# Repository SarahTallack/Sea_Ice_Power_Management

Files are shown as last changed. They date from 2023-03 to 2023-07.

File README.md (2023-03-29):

# Sea Ice Power Management

## Overview: 

The below extract is from the vacwork advertisement: 

“This work feeds into the physical characterisation of sea ice using LiDAR and cameras to improve parameterisation of Earth System Models. A preliminary prototype rig was constructed for the SCALE Winter 2022 cruise to collect data from a Livox AVIA LiDAR (https://www.livoxtech.com/avia) and an Intel Realsense D455 Depth camera (https://www.intelrealsense.com/depth-camera-d455). During the SCALE cruise we were able to collect a comprehensive LiDAR/Realsense scan dataset of individual pancake ice floes which were collected and placed on deck. The goal of these vacation work positions is to improve the reliability and usability of the imaging rig to make it more robust for future experiments and cruises.” 

This project focuses on the design and improvement of the power management for the rig mentioned in the above. This report aims to outline the process taken to understand the power requirements of the system, as well as to research possible methods for supplying power in cold weather (-20°C). 

## Design Process and Decisions 

Before exploring methods for supplying power, it is important to understand the power requirements of the system. Thus, the first step is to research individual components and determine what voltages they are able to operate at and draw up a power budget for the system. The power budget for the system is shown in the following section. 

Once a power budget had been compiled, a meeting was had to discuss the best methods for supplying power to the system. It was decided that a battery supply such a EcoFlow or Jackery would be the most robust and allow other groups to use the supply if needed. Since these batteries are Lithium-Ion, which operate best at room-temperature, a temperature controller enclosure needs to be designed for the battery. Additionally, the team wanted the system to be able to be powered from mains or from the battery, and to be able to easily switch between these two options. 

Thus, two separate circuits need to be designed. The first should be able to distribute a single supply to at least two devices, as well as to switch between either mains or a battery as the power supply. The second design needed to control the temperature of the box, using a microcontroller, sensors and heating pads. 

## Power Budget

The power budget can be found in an excel spreadsheet called PowerBudget.

## Power Distribution

### Basic Operation

Two devices needed to be power by a single source, namely an Intel NUC (mini-PC) and a Livox AVIA. These devices needed to either be powered by a main supply, via an AC/DC supply, or by a DC output from a battery supply. 

The user should be able to switch between the two supplies and turn everything off. A panel mounted switch is to be connected via the switch header pins (J6). An external LED indicator is connected in a similar fashion, using the J7 pins.  

A MOSFET configuration is used for switching when power is supplied, and the switch is ON. When Q1 is turned on, it allows Q2 to be turned on, which then provides power to the external jacks. Fuses are added to the output of each supply. 

Component Selection 

The input jacks had to be selected to ensure they could withstand up to 8A. 8A fuses are placed to ensure the circuit is not overloaded. Schottky diodes are chosen that can withstand the current to be supplied. 

N-channel MOSFETs are chosen for low current switching, and the P-channel MOSFET is selected as it can withstand high currents. The DC jacks at the output are selected to withstand up to 5A of current, which is the maximum current draw of the devices to be powered. 

### KiCAD project files

The project files for this board can be found in "\PCB Design\Power Distribution".

## Temperature Controller

### Basic Operation

The PCB is designed to fit onto an STM32 Nucleo-64 microcontroller. It is designed to read a temperature controller and implement a bang-bang controller to maintain the ambient temperature in an enclosure between a lower and upper temperature value, by switching external heating pads on or off.  

An RTD sensor is used in a Wheatstone bridge configuration, and the two outputs of the bridge are sent into an instrumentation amplifier (U1). The output of the instrumentation amplifier is sent to an ADC pin on the Nucleo. The Nucleo then converts this ADC value into a temperature. Depending on this temperature value, the heaters are either turned on or off.  

A GPIO output pin is used in conjunction with a MOSFET switching circuit, to supply an external power source to the heating pads, as the pads could not be powered by the microcontroller. 

A pushbutton is used to turn on and off the control, and an indicator is used to show if the system is operational or not.  

### KiCAD project files

The project files for this board can be found in "\PCB Design\Temperature Controller".

### STM Nucleo-64 Code

The code used for the temperature controller can be found in "\Temperature Control Code\TemperatureController".

## Component Selection and Calculations
Most calculations were done using the TemperatureSensorValues.mlx file. 

## Assembly and Testing of boards

## Other components needed

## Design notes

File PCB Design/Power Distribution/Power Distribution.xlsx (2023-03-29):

Source:,"C:\Users\sarah\Documents\sea-ice-power-management\PCB Design\Power Distribution\Power Distribution.kicad_sch"
Date:,"2022/12/08 15:22:51"
Tool:,"Eeschema (6.0.8)"
Generator:,"C:\Program Files\KiCad\6.0\bin\scripting\plugins/bom_csv_grouped_by_value.py"
Component Count:,"27"
Individual Components:
Item,"Qty","Reference(s)","Value","LibPart","Footprint","Datasheet","LCSC No.","Price"
,"","C1","10n","Device:C_Small","Capacitor_SMD:C_0805_2012Metric","https://datasheet.lcsc.com/lcsc/1811151136_Samsung-Electro-Mechanics-CL21B103KBANNNC_C1710.pdf","C1710","0.0062"
,"","C2","10n","Device:C_Small","Capacitor_SMD:C_0805_2012Metric","https://datasheet.lcsc.com/lcsc/1811151136_Samsung-Electro-Mechanics-CL21B103KBANNNC_C1710.pdf","C1710","0.0062"
,"","C3","100n","Device:C_Small","Capacitor_SMD:C_0805_2012Metric","https://datasheet.lcsc.com/lcsc/1810101813_YAGEO-CC0805KRX7R9BB104_C49678.pdf","C49678","0.0036"
,"","C4","4.7u","Device:C_Small","Capacitor_SMD:C_1206_3216Metric","https://datasheet.lcsc.com/lcsc/1811091112_FH--Guangdong-Fenghua-Advanced-Tech-1206B475K500NT_C29823.pdf","C29823","0.0091"
,"","D1","D_Schottky","Device:D_Schottky","Footprints:Schottky Diode SK1010C","https://datasheet.lcsc.com/lcsc/2012211036_MDD-Microdiode-Electronics--SK1010C_C65020.pdf","C65020","0.1616"
,"","D2","D_Schottky","Device:D_Schottky","Footprints:Schottky Diode SK1010C","https://datasheet.lcsc.com/lcsc/2012211036_MDD-Microdiode-Electronics--SK1010C_C65020.pdf","C65020","0.1616"
,"","F1","Fuse","Device:Fuse","Footprints:FUSE Holder ROHS","https://datasheet.lcsc.com/lcsc/1811061209_Xucheng-Elec-C3131_C3131.pdf","C3131","0.0590"
,"","F2","Fuse","Device:Fuse","Footprints:FUSE Holder ROHS","https://datasheet.lcsc.com/lcsc/1811061209_Xucheng-Elec-C3131_C3131.pdf","C3131","0.0590"
,"","J1","Barrel_Jack",":Barrel_Jack_1","Footprints:CONN-TH_XT60PW-M","https://datasheet.lcsc.com/lcsc/1810251313_Changzhou-Amass-Elec-XT60PW-M_C98732.pdf","C98732","0.3915"
,"","J2","Barrel_Jack",":Barrel_Jack_1","Footprints:CONN-TH_XT60PW-M","https://datasheet.lcsc.com/lcsc/1810251313_Changzhou-Amass-Elec-XT60PW-M_C98732.pdf","C98732","0.3915"
,"","J3","Barrel_Jack","SarahLibrary:Barrel_Jack","Footprints:DC Jack 5A","https://datasheet.lcsc.com/lcsc/2110151730_XKB-Connectivity-DC-005-5A-3-0_C388625.pdf","C388625","0.2379"
,"","J4","Barrel_Jack","SarahLibrary:Barrel_Jack","Footprints:DC Jack 5A","https://datasheet.lcsc.com/lcsc/2110151730_XKB-Connectivity-DC-005-5A-3-0_C388625.pdf","C388625","0.2379"
,"","J5","Barrel_Jack","SarahLibrary:Barrel_Jack","Footprints:DC Jack 5A","https://datasheet.lcsc.com/lcsc/2110151730_XKB-Connectivity-DC-005-5A-3-0_C388625.pdf","C388625","0.2379"
,"","J6","Switch Header Pin","Connector:Conn_01x03_Male","Footprints:3 Pin Male Header","https://datasheet.lcsc.com/lcsc/1811021622_BOOMELE-Boom-Precision-Elec-VH-3A_C20547.pdf","C20547","0.0303"
,"","J7","Conn_01x02_Male","Connector:Conn_01x02_Male","Footprints:2 Pin Male Header","https://datasheet.lcsc.com/lcsc/1811132110_BOOMELE-Boom-Precision-Elec-XH-2A_C20079.pdf","C20079","0.0058"
,"","Q1","2N7002","Transistor_FET:2N7002","Package_TO_SOT_SMD:SOT-23","https://datasheet.lcsc.com/lcsc/1810151612_Jiangsu-Changjing-Electronics-Technology-Co---Ltd--2N7002_C8545.pdf","C8545","0.0149"
,"","Q2","NCE30P30K","SarahLibrary:NCE30P30K","Footprints:NCE30P30K P channel MOSFET","https://datasheet.lcsc.com/lcsc/1811041601_Wuxi-NCE-Power-Semiconductor-NCE30P30K_C130106.pdf","C130106","0.1349"
,"","Q3","2N7002","Transistor_FET:2N7002","Package_TO_SOT_SMD:SOT-23","https://datasheet.lcsc.com/lcsc/1810151612_Jiangsu-Changjing-Electronics-Technology-Co---Ltd--2N7002_C8545.pdf","C8545","0.0149"
,"","R1","330k","Device:R","Resistor_SMD:R_0805_2012Metric","https://datasheet.lcsc.com/lcsc/2205311830_UNI-ROYAL-Uniroyal-Elec-0805W8F3303T5E_C17629.pdf","C17629","0.0015"
,"","R2","10k","Device:R","Resistor_SMD:R_0805_2012Metric","https://datasheet.lcsc.com/lcsc/2206010216_UNI-ROYAL-Uniroyal-Elec-0805W8F1002T5E_C17414.pdf","C17414","0.0008"
,"","R3","100k","Device:R","Resistor_SMD:R_0805_2012Metric","https://datasheet.lcsc.com/lcsc/2205312316_UNI-ROYAL-Uniroyal-Elec-0805W8F1003T5E_C149504.pdf","C149504","0.0016"
,"","R4","82k","Device:R","Resistor_SMD:R_0805_2012Metric","https://datasheet.lcsc.com/lcsc/2205311830_UNI-ROYAL-Uniroyal-Elec-0805W8F8202T5E_C17840.pdf","C17840","0.0016"
,"","R5","100k","Device:R","Resistor_SMD:R_0805_2012Metric","https://datasheet.lcsc.com/lcsc/2205312316_UNI-ROYAL-Uniroyal-Elec-0805W8F1003T5E_C149504.pdf","C149504","0.0016"
,"","R6","1.8k","Device:R","Resistor_SMD:R_0805_2012Metric","https://datasheet.lcsc.com/lcsc/2206010216_UNI-ROYAL-Uniroyal-Elec-0805W8F1801T5E_C17398.pdf","C17398","0.0016"
,"","TP1","TestPoint","Connector:TestPoint","TestPoint:TestPoint_Plated_Hole_D2.0mm","~","",""
,"","TP2","TestPoint","Connector:TestPoint","TestPoint:TestPoint_Plated_Hole_D2.0mm","~","",""
,"","TP3","TestPoint","Connector:TestPoint","TestPoint:TestPoint_Plated_Hole_D2.0mm","~","",""
Collated Components:
Item,"Qty","Reference(s)","Value","LibPart","Footprint","Datasheet","LCSC No.","Price"
1,"2","C1, C2","10n","Device:C_Small","Capacitor_SMD:C_0805_2012Metric","https://datasheet.lcsc.com/lcsc/1811151136_Samsung-Electro-Mechanics-CL21B103KBANNNC_C1710.pdf","C1710","0.0062"
2,"1","C3","100n","Device:C_Small","Capacitor_SMD:C_0805_2012Metric","https://datasheet.lcsc.com/lcsc/1810101813_YAGEO-CC0805KRX7R9BB104_C49678.pdf","C49678","0.0036"
3,"1","C4","4.7u","Device:C_Small","Capacitor_SMD:C_1206_3216Metric","https://datasheet.lcsc.com/lcsc/1811091112_FH--Guangdong-Fenghua-Advanced-Tech-1206B475K500NT_C29823.pdf","C29823","0.0091"
4,"2","D1, D2","D_Schottky","Device:D_Schottky","Footprints:Schottky Diode SK1010C","https://datasheet.lcsc.com/lcsc/2012211036_MDD-Microdiode-Electronics--SK1010C_C65020.pdf","C65020","0.1616"
5,"2","F1, F2","Fuse","Device:Fuse","Footprints:FUSE Holder ROHS","https://datasheet.lcsc.com/lcsc/1811061209_Xucheng-Elec-C3131_C3131.pdf","C3131","0.0590"
6,"2","J1, J2","Barrel_Jack",":Barrel_Jack_1","Footprints:CONN-TH_XT60PW-M","https://datasheet.lcsc.com/lcsc/1810251313_Changzhou-Amass-Elec-XT60PW-M_C98732.pdf","C98732","0.3915"
7,"3","J3, J4, J5","Barrel_Jack","SarahLibrary:Barrel_Jack","Footprints:DC Jack 5A","https://datasheet.lcsc.com/lcsc/2110151730_XKB-Connectivity-DC-005-5A-3-0_C388625.pdf","C388625","0.2379"
8,"1","J6","Switch Header Pin","Connector:Conn_01x03_Male","Footprints:3 Pin Male Header","https://datasheet.lcsc.com/lcsc/1811021622_BOOMELE-Boom-Precision-Elec-VH-3A_C20547.pdf","C20547","0.0303"
9,"1","J7","Conn_01x02_Male","Connector:Conn_01x02_Male","Footprints:2 Pin Male Header","https://datasheet.lcsc.com/lcsc/1811132110_BOOMELE-Boom-Precision-Elec-XH-2A_C20079.pdf","C20079","0.0058"
10,"2","Q1, Q3","2N7002","Transistor_FET:2N7002","Package_TO_SOT_SMD:SOT-23","https://datasheet.lcsc.com/lcsc/1810151612_Jiangsu-Changjing-Electronics-Technology-Co---Ltd--2N7002_C8545.pdf","C8545","0.0149"
11,"1","Q2","NCE30P30K","SarahLibrary:NCE30P30K","Footprints:NCE30P30K P channel MOSFET","https://datasheet.lcsc.com/lcsc/1811041601_Wuxi-NCE-Power-Semiconductor-NCE30P30K_C130106.pdf","C130106","0.1349"
12,"1","R1","330k","Device:R","Resistor_SMD:R_0805_2012Metric","https://datasheet.lcsc.com/lcsc/2205311830_UNI-ROYAL-Uniroyal-Elec-0805W8F3303T5E_C17629.pdf","C17629","0.0015"
13,"1","R2","10k","Device:R","Resistor_SMD:R_0805_2012Metric","https://datasheet.lcsc.com/lcsc/2206010216_UNI-ROYAL-Uniroyal-Elec-0805W8F1002T5E_C17414.pdf","C17414","0.0008"
14,"2","R3, R5","100k","Device:R","Resistor_SMD:R_0805_2012Metric","https://datasheet.lcsc.com/lcsc/2205312316_UNI-ROYAL-Uniroyal-Elec-0805W8F1003T5E_C149504.pdf","C149504","0.0016"
15,"1","R4","82k","Device:R","Resistor_SMD:R_0805_2012Metric","https://datasheet.lcsc.com/lcsc/2205311830_UNI-ROYAL-Uniroyal-Elec-0805W8F8202T5E_C17840.pdf","C17840","0.0016"
16,"1","R6","1.8k","Device:R","Resistor_SMD:R_0805_2012Metric","https://datasheet.lcsc.com/lcsc/2206010216_UNI-ROYAL-Uniroyal-Elec-0805W8F1801T5E_C17398.pdf","C17398","0.0016"
17,"3","TP1, TP2, TP3","TestPoint","Connector:TestPoint","TestPoint:TestPoint_Plated_Hole_D2.0mm","~","",""

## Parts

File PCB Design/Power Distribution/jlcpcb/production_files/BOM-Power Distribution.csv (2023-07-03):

Comment | Designator | Footprint | LCSC
NCE30P30K | Q2 | TO-252-2 | C130106
10n | C1,C2 | C_0402_1005Metric | C15195
1.8k | R6 | R_0805_2012Metric | C17398
82k | R4 | R_0805_2012Metric | C17840
LED | J7 | 2 Pin Male Header | C20079
Switch Header Pin | J6 | PinHeader_1x03_P2.54mm_Vertical | C20547
100k | R3,R5 | R_0402_1005Metric | C25741
10k | R2 | R_0402_1005Metric | C25744
330k | R1 | R_0402_1005Metric | C25778
4.7u | C4 | C_1206_3216Metric | C29823
100n | C3 | C_0402_1005Metric | C307331
Fuse | F1,F2 | FUSE Holder ROHS | C3131
Barrel_Jack | J3,J4,J5 | DC Jack 5A | C388625
D_Schottky | D1,D2 | Schottky Diode SK1010C | C65020
2N7002 | Q1,Q3 | SOT-23 | C8545
Barrel_Jack | J1,J2 | CONN-TH_XT60PW-M | C98732
TestPoint | TP1 | TestPoint_THTPad_D1.0mm_Drill0.5mm
TestPoint | TP2 | TestPoint_THTPad_D1.0mm_Drill0.5mm
TestPoint | TP3 | TestPoint_THTPad_D1.0mm_Drill0.5mm
Conn_01x02_Pin | J8 | PinHeader_1x02_P2.54mm_Vertical
Conn_01x02_Pin | J9 | PinHeader_1x02_P2.54mm_Vertical

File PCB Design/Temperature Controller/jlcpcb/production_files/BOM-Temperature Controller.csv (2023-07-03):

Comment | Designator | Footprint | LCSC
CJ431 | U2 | SOT-23 | C171428
INA332 | U1 | VSSOP-8_3.0x3.0mm_P0.65mm | C181461
PT100 Header Pins | J1,J2,J3 | 2 Pin Male Header | C20079
S8050_SMD | Q3 | SOT-23 | C2146
1.1k | R7 | R_0603_1608Metric | C22764
1.2k | R12,R6 | R_0603_1608Metric | C22765
Red | D2 | D_0603_1608Metric | C2286
27k | R5 | R_0603_1608Metric | C22967
3.3k | R1,R2 | R_0603_1608Metric | C22978
10k | R8 | R_0603_1608Metric | C25804
91 | R3 | R_0603_1608Metric | C2960792
SANYOU_SRD_Form_C | K1 | Relay_SPDT_SANYOU_SRD_Series_Form_C | C35449
Barrel_Jack | J5 | DC Jack 5A | C388625
Conn_01x03_Male | J8 | TerminalBlock_Altech_AK300-3_P5.00mm | C72334
1N5819 | D1 | D_SOD-123 | C8598
10u | C4 | C_0603_1608Metric | C96446
TestPoint | TP5 | TestPoint_THTPad_D1.0mm_Drill0.5mm
TestPoint | TP9 | TestPoint_Pad_D1.5mm
TestPoint | TP2 | TestPoint_THTPad_D1.0mm_Drill0.5mm
TestPoint | TP7 | TestPoint_THTPad_D1.0mm_Drill0.5mm
TestPoint | TP8 | TestPoint_Pad_D1.5mm
TestPoint | TP6 | TestPoint_THTPad_D1.0mm_Drill0.5mm
TestPoint | TP4 | TestPoint_THTPad_D1.0mm_Drill0.5mm
TestPoint | TP1 | TestPoint_THTPad_D1.0mm_Drill0.5mm
TestPoint | TP3 | TestPoint_THTPad_D1.0mm_Drill0.5mm
Conn_01x19_Female | J7 | PinSocket_1x19_P2.54mm_Vertical
Conn_01x19_Female | J6 | PinSocket_1x19_P2.54mm_Vertical

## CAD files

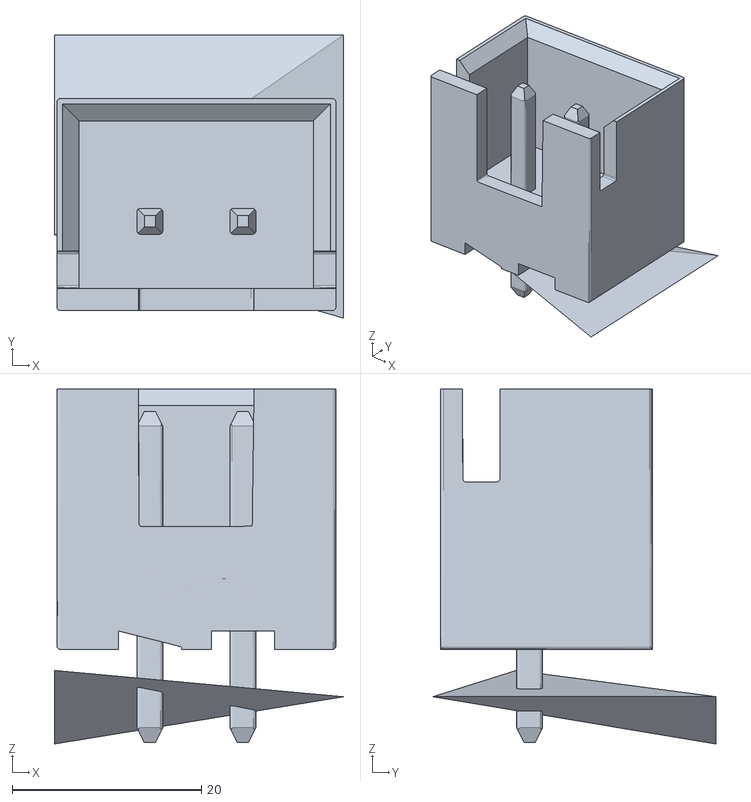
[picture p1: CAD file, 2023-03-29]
PCB Design/3D Model/2 Pin Header.obj
30.6 x 30.0 x 37.6

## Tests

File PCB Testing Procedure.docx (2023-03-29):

## Power Distribution

Circuits have been built/tested on a breadboard before ordering PCB. Theoretically should work.

### Steps for testing (before power)

1. Check that all components are populated that needed to be (also check orientation if applicable) - if there are any missing then these should be added before continuing.
2. Check most basic connections using test points and terminals.

The following tests should be done without inserting the fuses or connecting anything to the outputs.

### Test 1: check input (no fuse inserted)

1. Check that the input terminal works (was the actual circuit correct). If V+ and ground are connected is that what the board will get supplied with.

### Test 2: testing the switching circuit

1. Check resistor values.
2. Connect 12V to the Supply test point (probably should have had header pins here instead of a test point).
3. Check that the toggle switch works as expected with circuit.
4. Check that following is true:
5. Connect LED to J7 and check that it also only switches on when Vout is high.

### Test 3: check output

1. Supply voltage to Vout and check that barrel jacks at output have this voltage. Once again would have been useful to have header pins here instead of just a testpoint.
2. Barrel jacks should have V+ in centre rod and GND on the outer ring (bottom connector)

### Notes

- Should have included more header pins, especially for powering the circuits separately for testing and fault finding.

## Temperature Controller

### Steps for testing (before power)

1. Check that all components are populated that needed to be (also check orientation if applicable) - if there are any missing then these should be added before continuing.
2. Check most basic connections using test points and terminals.

Unit tests for temperature controller PCB

### Test 1: check wheatstone bridge

1. Check that resistor values.
2. Connect PT100 (need to get MOLEX connectors for this) or could use potentiometer to vary this value manually – just need to ensure that the resistor values from the pot are the same as range expected for PT100.

### Test 2: Instrumentation amplifier testing

1. If all connections are correct can power using +3V3 (this circuit is only connected to the wheatstone bridge)
2. Vary the voltage at Va (can either use jumpers and breadboard connected to J1 and manually swap out resistors or use a potentiometer).
3. Scope TempReading testpoint and compare value for various resistors to the expected/calculated values (should have a MATLAB script to do this).

### Test 3: inputs and outputs

1. Check connections and resistor values.
2. Connect the push button and LED and check that the circuit works.
3. Check barrel jack connections.

### Test 4: Relay circuit

1. Missing components are for the relay circuit – just need to talk to Justin about this.
2. Check that switching circuit works with a voltage of 3V3 at PD2 (this would be from the microcontroller).
3. Check that voltage across COM and NO only go high when PD2 goes high.

### Test 5: Temperature control code

1. Retest code developed previously.
2. Connect output from instrumentation amplifier only – use UART to print out the values being read for specific resistors values (check that ADC and code works properly). Should use same resistors/values as in test 2 step 3.
3. Disconnect instrumentation output. Connect the GPIO pins to the push button and LED and check that these work with code.
4. Check that the orientation of the board is correct so that it can fit onto the STM Nucleo.

### Notes

- Board was designed to use be power by the Nucleo via the micro-USB.
- Barrel jack power input is only for the relay circuit.
- Looking back – would have added a voltage regulator circuit to get a 5V output from the 12V which could be used to power the board and supply power to the relays.

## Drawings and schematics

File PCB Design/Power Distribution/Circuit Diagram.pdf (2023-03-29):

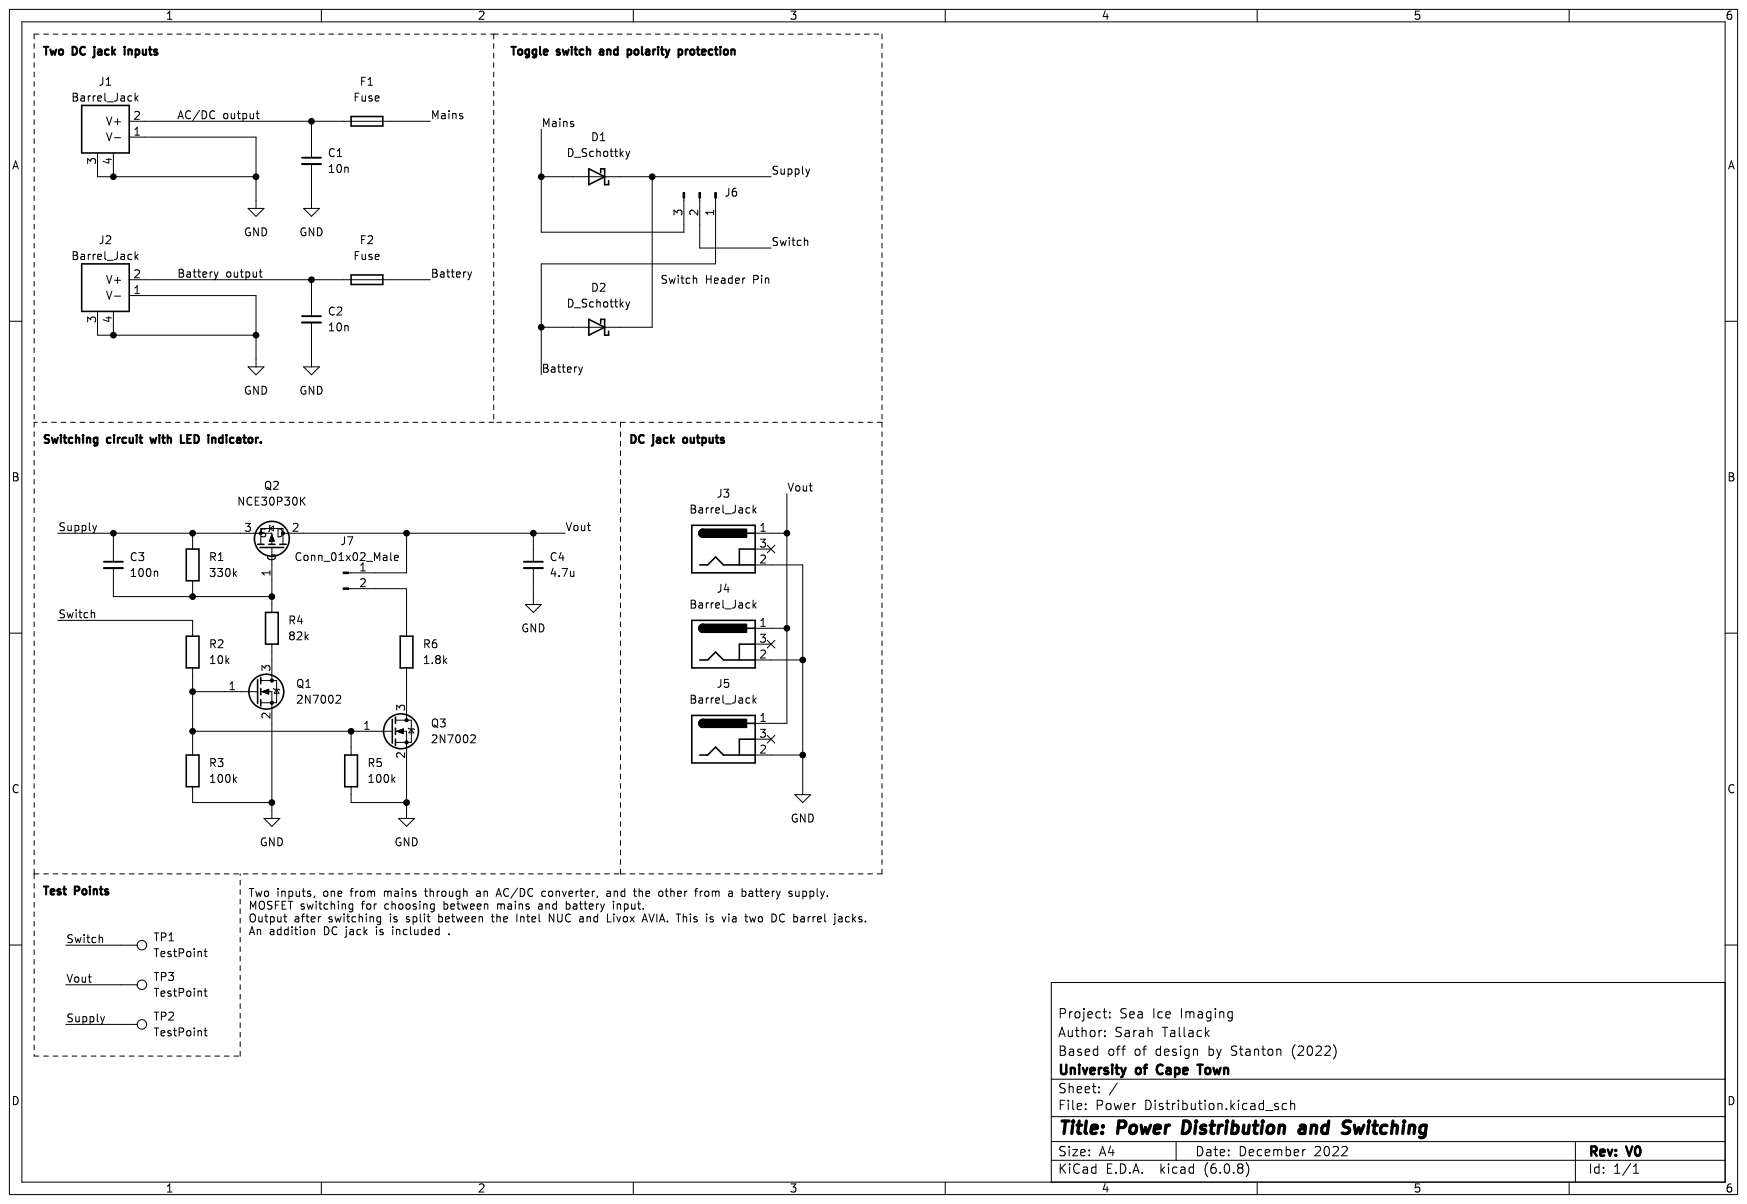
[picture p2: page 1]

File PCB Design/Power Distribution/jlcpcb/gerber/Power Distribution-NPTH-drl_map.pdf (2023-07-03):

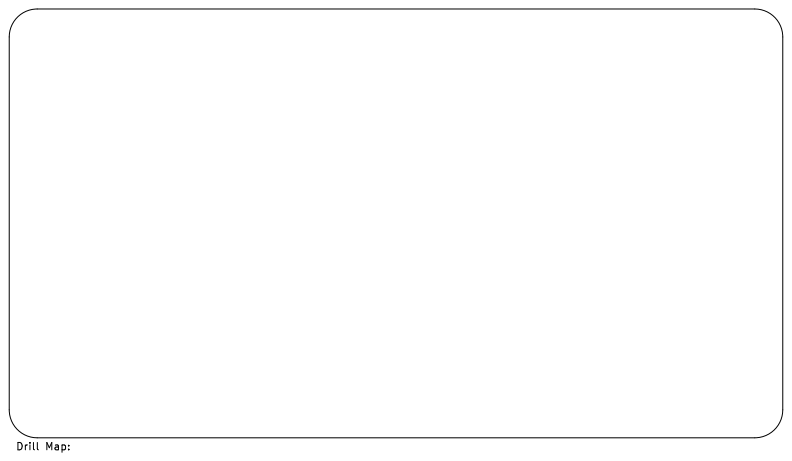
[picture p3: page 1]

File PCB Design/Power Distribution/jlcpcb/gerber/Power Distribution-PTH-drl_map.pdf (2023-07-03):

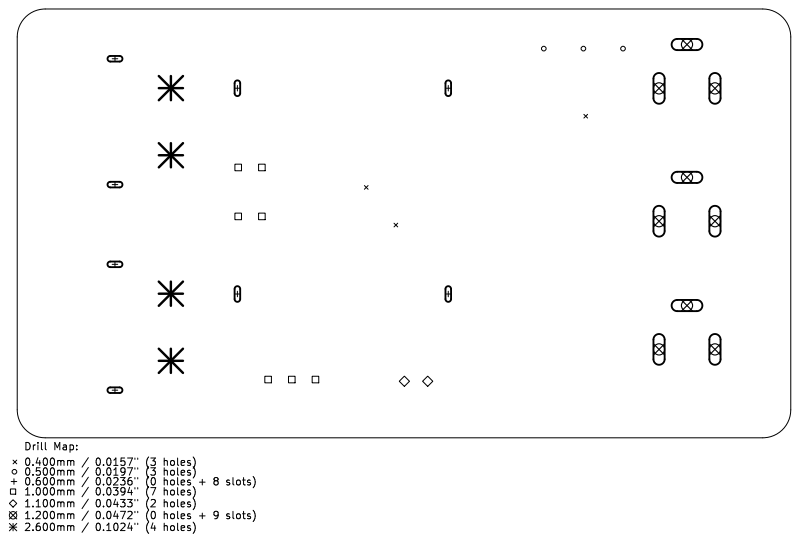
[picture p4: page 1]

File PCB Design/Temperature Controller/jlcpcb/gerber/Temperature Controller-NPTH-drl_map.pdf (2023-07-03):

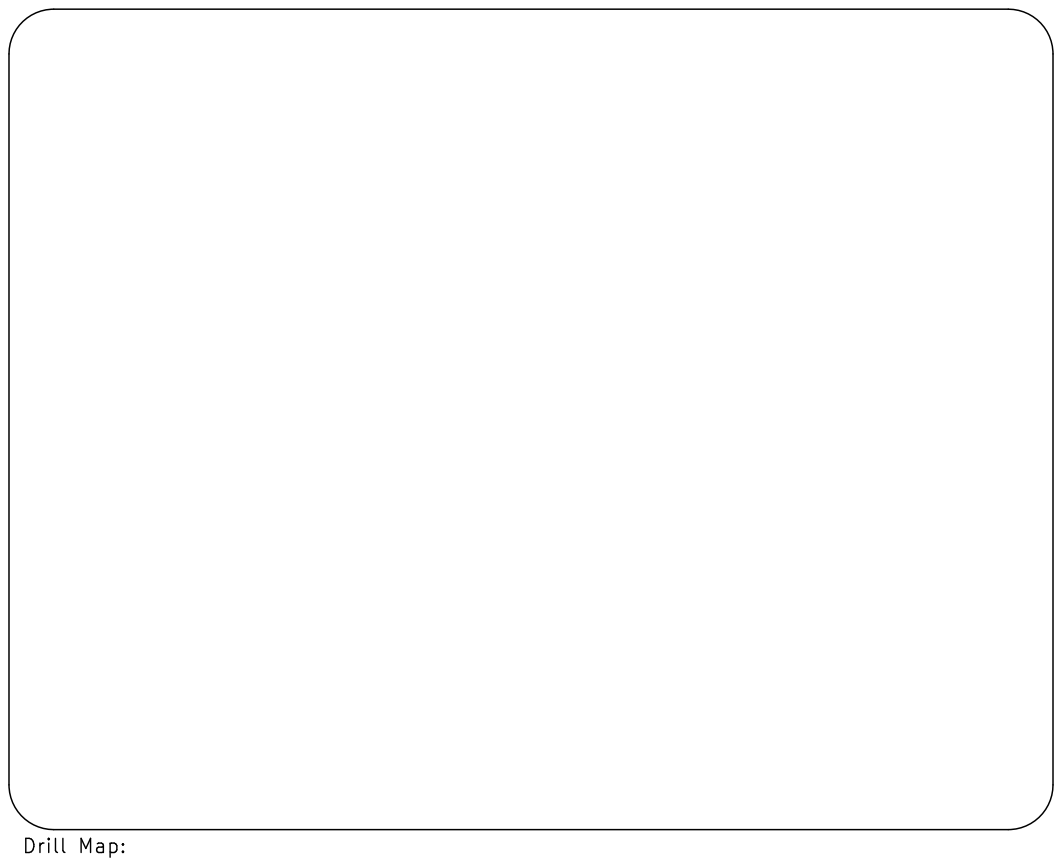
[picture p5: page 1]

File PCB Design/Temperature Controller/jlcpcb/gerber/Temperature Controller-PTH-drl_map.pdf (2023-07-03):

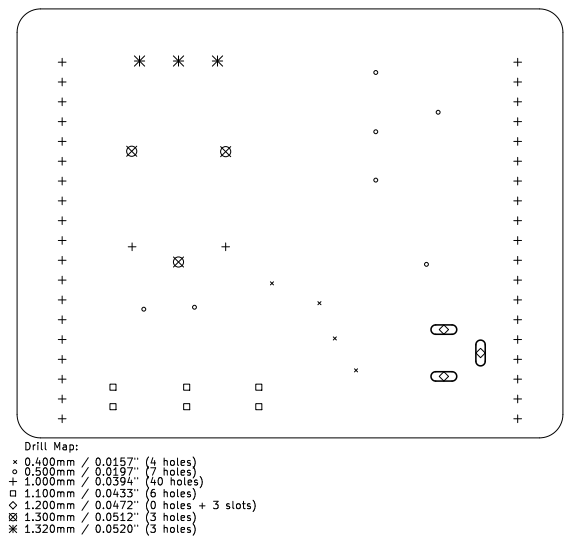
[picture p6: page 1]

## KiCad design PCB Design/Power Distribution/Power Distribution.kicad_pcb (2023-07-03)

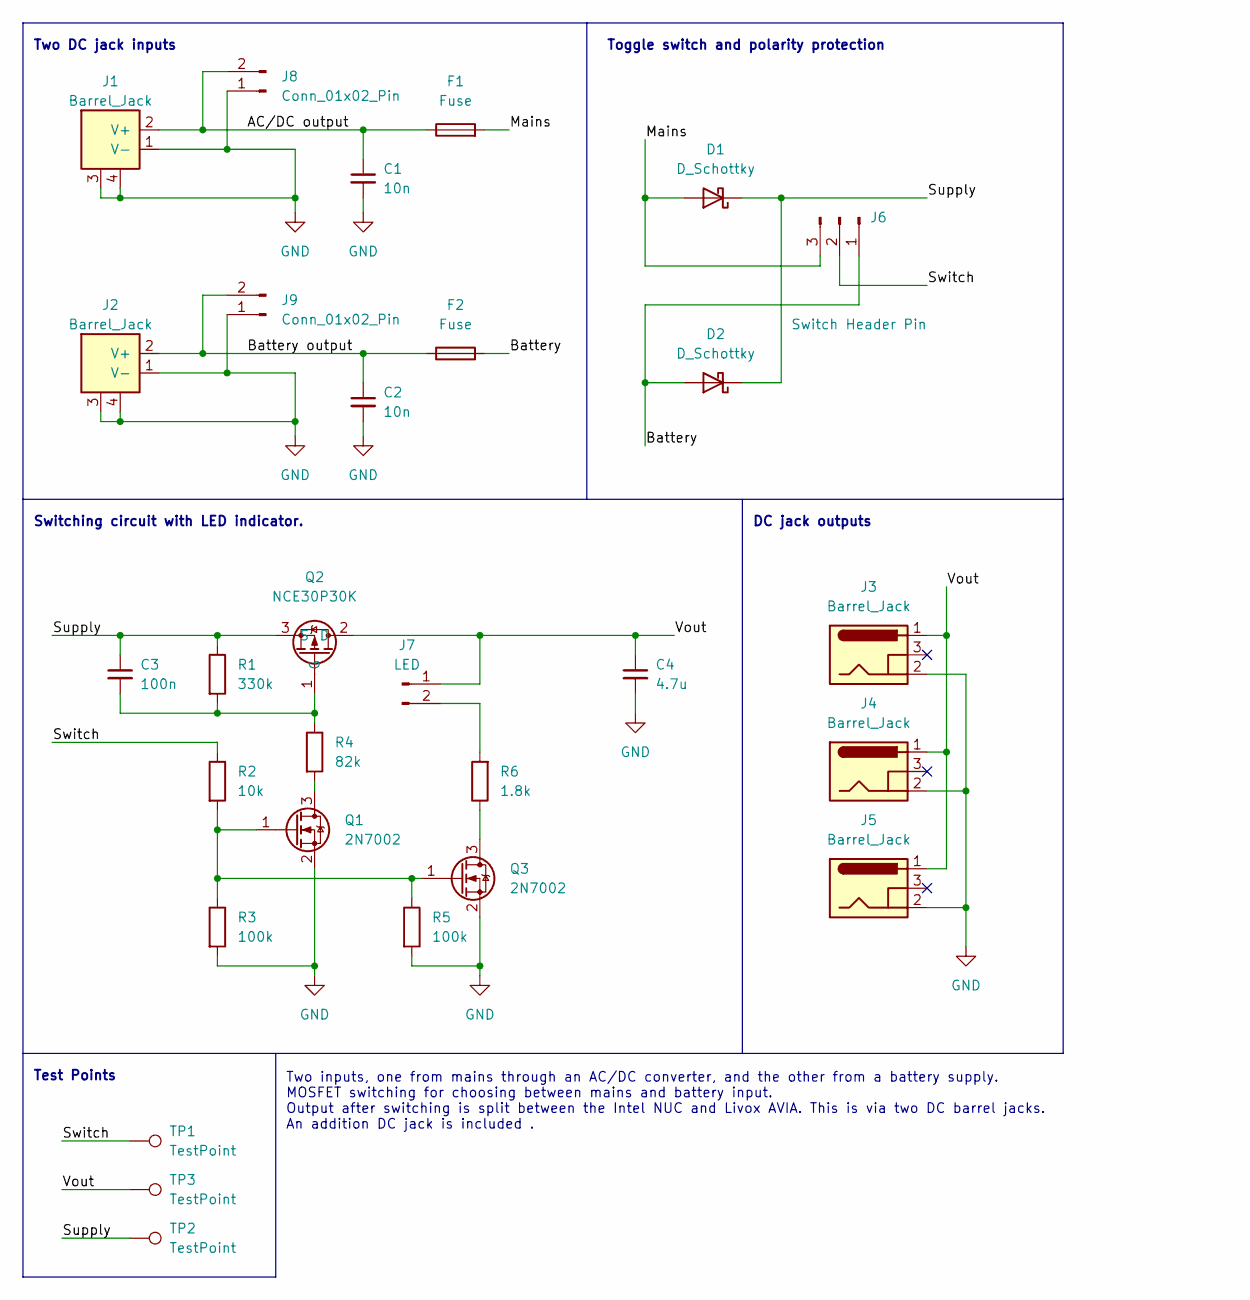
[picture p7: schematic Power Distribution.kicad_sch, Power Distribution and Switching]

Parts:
C1, C2: 10n; C_0402_1005Metric; LCSC C15195
C3: 100n; C_0402_1005Metric; LCSC C307331
C4: 4.7u; C_1206_3216Metric; LCSC C29823
D1, D2: D_Schottky; Schottky Diode SK1010C; LCSC C65020
F1, F2: Fuse; FUSE Holder ROHS; LCSC C3131
J1, J2: Barrel_Jack; CONN-TH_XT60PW-M; LCSC C98732
J3, J4, J5: Barrel_Jack; DC Jack 5A; LCSC C388625
J6: Switch Header Pin; PinHeader_1x03_P2.54mm_Vertical
J7: LED; 2 Pin Male Header
J8, J9: Conn_01x02_Pin; PinHeader_1x02_P2.54mm_Vertical
Q1, Q3: 2N7002; SOT-23; LCSC C8545
Q2: NCE30P30K; TO-252-2; LCSC C130106
R1: 330k; R_0402_1005Metric; LCSC C25778
R2: 10k; R_0402_1005Metric; LCSC C25744
R3, R5: 100k; R_0402_1005Metric; LCSC C25741
R4: 82k; R_0805_2012Metric; LCSC C17840
R6: 1.8k; R_0805_2012Metric; LCSC C17398
TP1, TP2, TP3: TestPoint; TestPoint_THTPad_D1.0mm_Drill0.5mm

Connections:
/AC/DC output: C1.1, F1.1, J1.2 (V+), J8.2
/Battery: D2.2 (A), F2.2, J6.1
/Battery output: C2.1, F2.1, J2.2 (V+), J9.2
/Mains: D1.2 (A), F1.2, J6.3
/Supply: C3.1, D1.1 (K), D2.1 (K), Q2.3 (S), R1.1, TP2.1
/Switch: J6.2, R2.1, TP1.1
/Vout: C4.1, J3.1, J4.1, J5.1, J7.1, Q2.2 (D), TP3.1
GND: C1.2, C2.2, C4.2, J1.1 (V-), J1.3, J1.4, J2.1 (V-), J2.3, J2.4, J3.2, J4.2, J5.2, J8.1, J9.1, Q1.2 (S), Q3.2 (S), R3.2, R5.2
unnamed: J7.2, R6.2
unnamed: Q1.3 (D), R4.2
unnamed: Q1.1 (G), Q3.1 (G), R2.2, R3.1, R5.1
unnamed: C3.2, Q2.1 (G), R1.2, R4.1
unnamed: Q3.3 (D), R6.1

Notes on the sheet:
Toggle switch and polarity protection
Two inputs, one from mains through an AC/DC converter, and the other from a battery supply. MOSFET switching for choosing between mains and battery input. Output after switching is split between the Intel NUC and Livox AVIA. This is via two DC barrel jacks. An addition DC jack is included .
Test Points
Switching circuit with LED indicator.
DC jack outputs
Two DC jack inputs

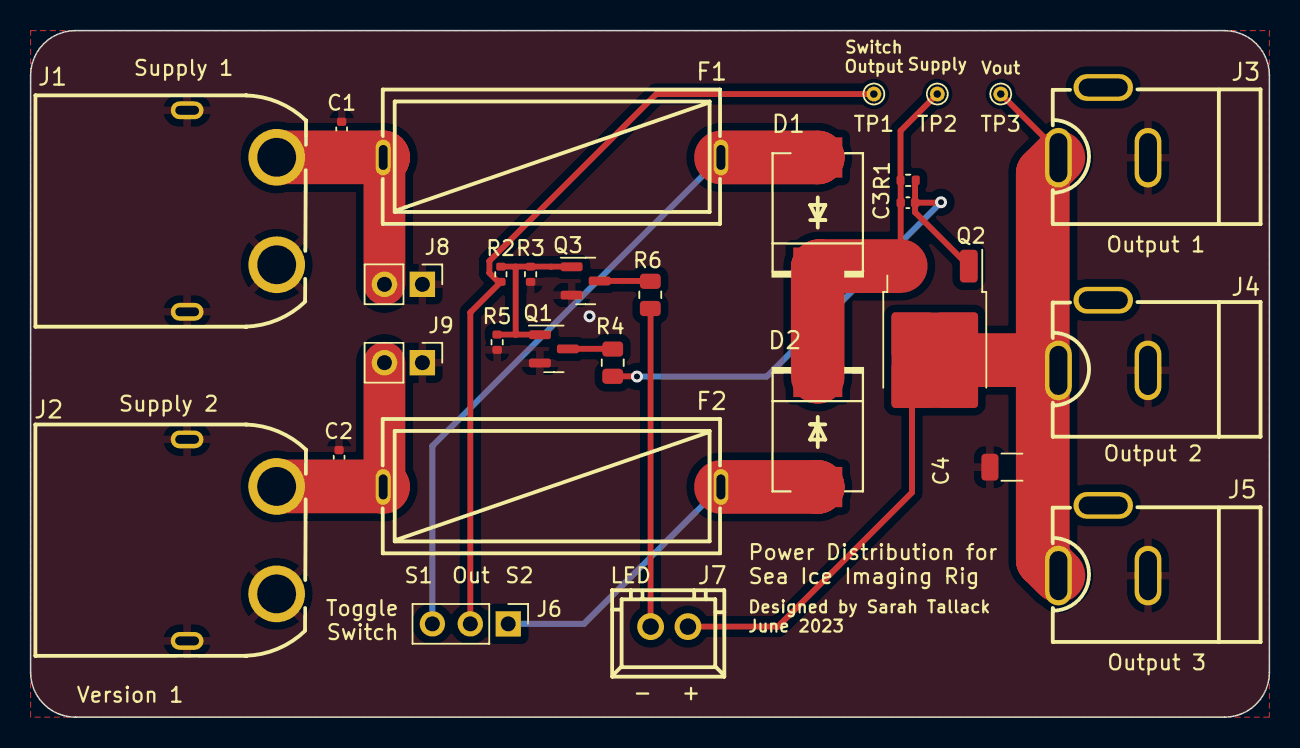
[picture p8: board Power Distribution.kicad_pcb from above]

Board: 2 copper layers, 83.0 x 46.0 mm, 29 parts (0 on the bottom side), 13 nets.

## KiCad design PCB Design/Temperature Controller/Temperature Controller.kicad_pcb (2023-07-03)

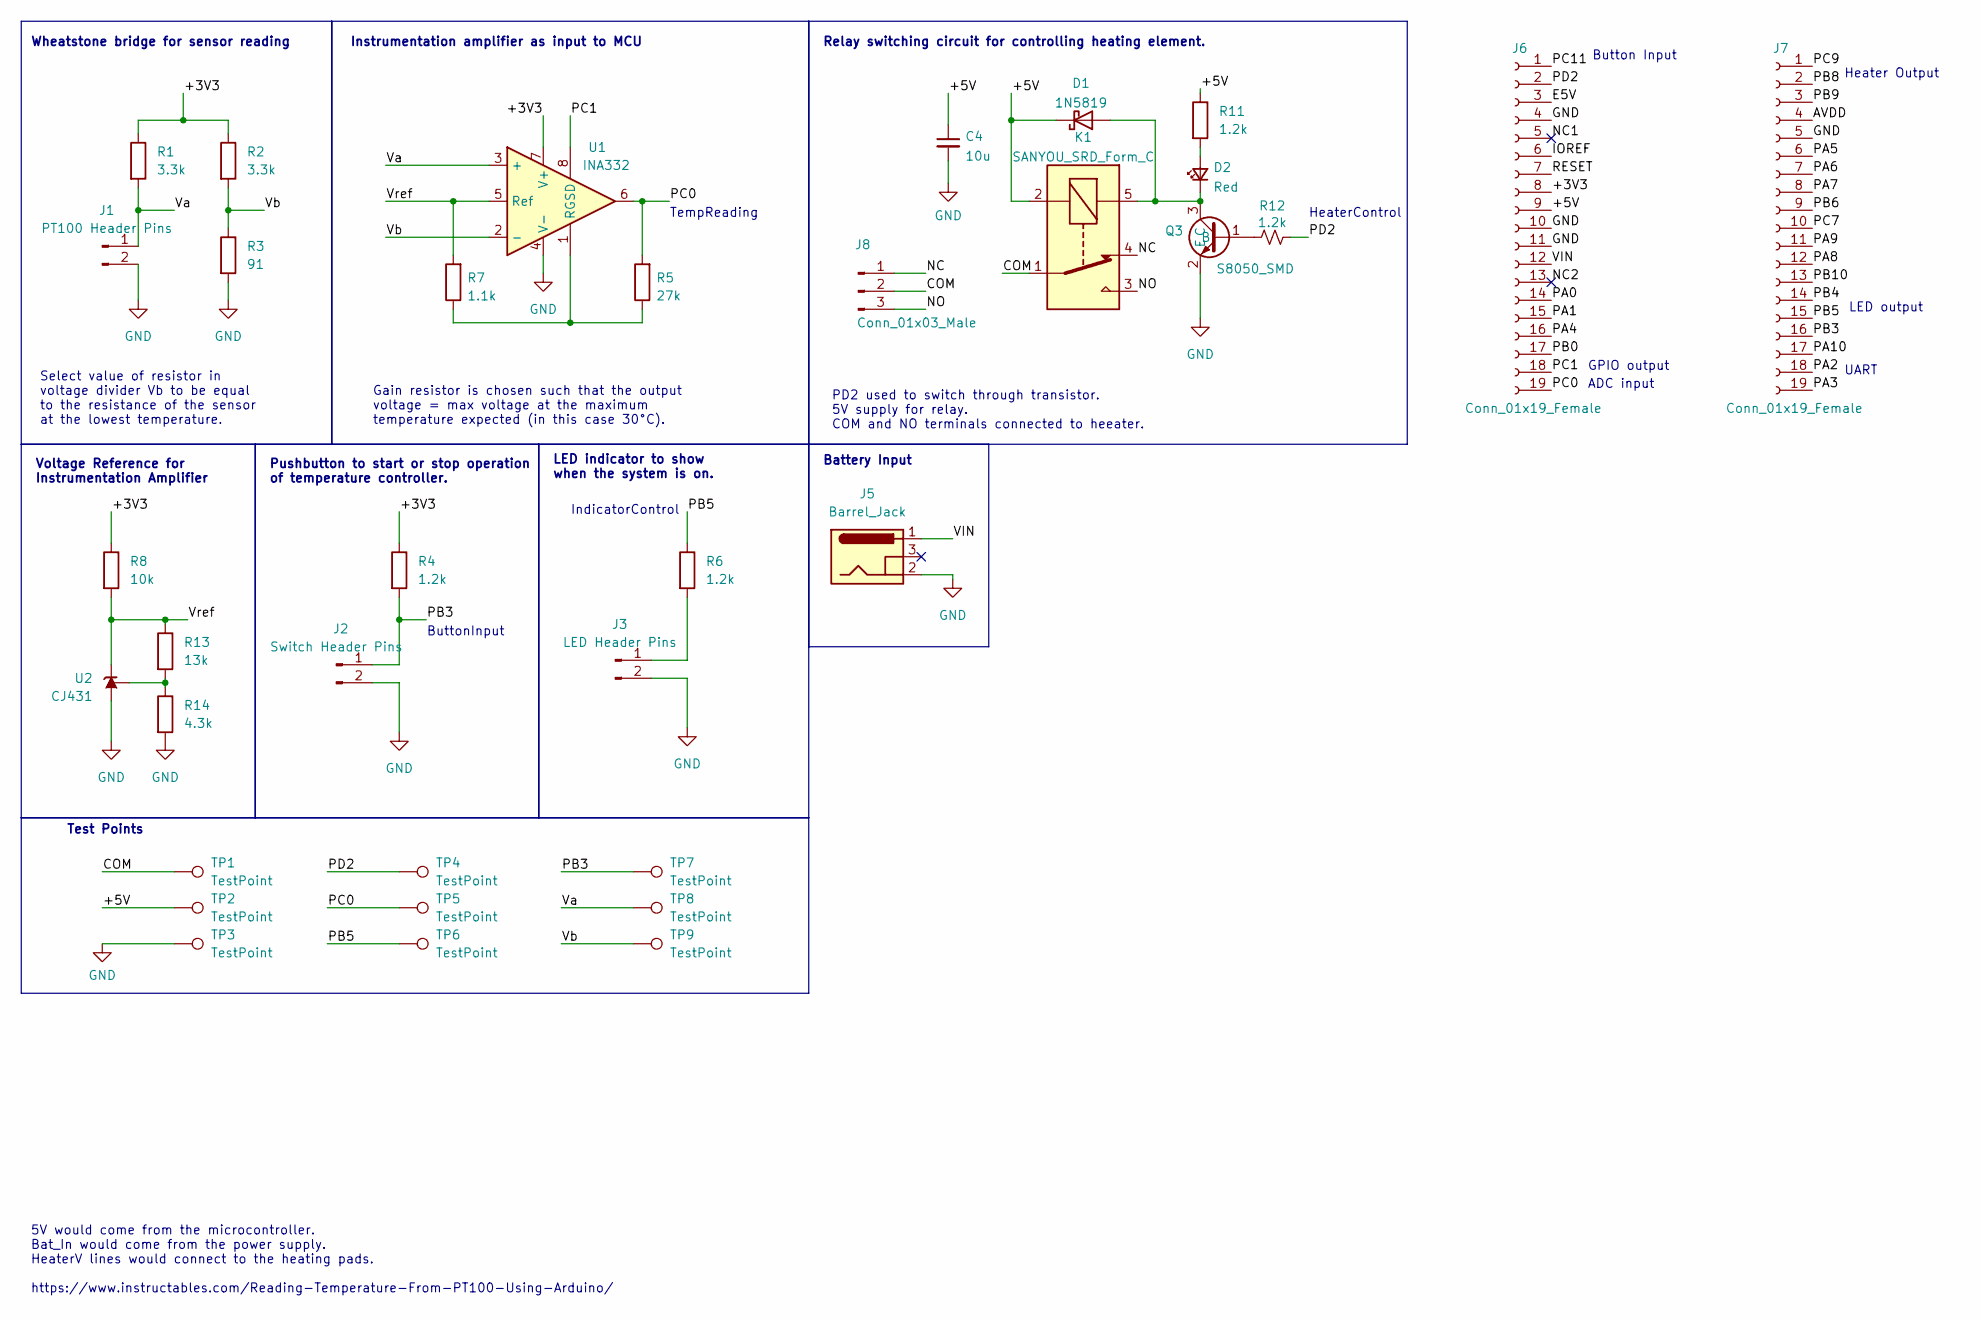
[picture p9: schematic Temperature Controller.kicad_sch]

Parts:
C4: 10u; C_0603_1608Metric; LCSC C96446
D1: 1N5819; D_SOD-123; LCSC C8598
D2: Red; D_0603_1608Metric; LCSC C2286
J1: PT100 Header Pins; 2 Pin Male Header; LCSC C20079
J2: Switch Header Pins; 2 Pin Male Header; LCSC C20079
J3: LED Header Pins; 2 Pin Male Header; LCSC C20079
J5: Barrel_Jack; DC Jack 5A; LCSC C388625
J6, J7: Conn_01x19_Female; PinSocket_1x19_P2.54mm_Vertical
J8: Conn_01x03_Male; TerminalBlock_Altech_AK300-3_P5.00mm; LCSC C72334
K1: SANYOU_SRD_Form_C; Relay_SPDT_SANYOU_SRD_Series_Form_C; LCSC C35449
Q3: S8050_SMD; SOT-23; LCSC C2146
R1, R2: 3.3k; R_0603_1608Metric; LCSC C22978
R3: 91; R_0603_1608Metric; LCSC C2960792
R4, R6, R11, R12: 1.2k; R_0603_1608Metric; LCSC C22765
R5: 27k; R_0603_1608Metric; LCSC C22967
R7: 1.1k; R_0603_1608Metric; LCSC C22764
R8: 10k; R_0603_1608Metric; LCSC C25804
R13: 13k; R_0603_1608Metric; LCSC C22797
R14: 4.3k; R_0603_1608Metric; LCSC C23159
TP1, TP2, TP3, TP4, TP5, TP6, TP7: TestPoint; TestPoint_THTPad_D1.0mm_Drill0.5mm
TP8, TP9: TestPoint; TestPoint_Pad_D1.5mm
U1: INA332; VSSOP-8_3.0x3.0mm_P0.65mm; LCSC C181461
U2: CJ431; SOT-23; LCSC C171428

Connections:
/+3V3: J6.8, R1.1, R2.1, R4.1, R8.1, U1.7 (V+)
/+5V: C4.1, D1.1 (K), J6.9, K1.2, R11.1, TP2.1
/AVDD: J7.4
/COM: J8.2, K1.1, TP1.1
/E5V: J6.3
/IOREF: J6.6
/NC: J8.1, K1.4
/NC1: J6.5
/NC2: J6.13
/NO: J8.3, K1.3
/PA0: J6.14
/PA1: J6.15
/PA2: J7.18
/PA3: J7.19
/PA4: J6.16
/PA5: J7.6
/PA6: J7.7
/PA7: J7.8
/PA8: J7.12
/PA9: J7.11
/PA10: J7.17
/PB0: J6.17
/PB3: J2.1, J7.16, R4.2, TP7.1
/PB4: J7.14
/PB5: J7.15, R6.1, TP6.1
/PB6: J7.9
/PB8: J7.2
/PB9: J7.3
/PB10: J7.13
/PC0: J6.19, R5.2, TP5.1, U1.6
/PC1: J6.18, U1.8 (SD)
/PC7: J7.10
/PC9: J7.1
/PC11: J6.1
/PD2: J6.2, R12.2, TP4.1
/RESET: J6.7
/VIN: J5.1, J6.12
/Va: J1.1, R1.2, TP8.1, U1.3 (+)
/Vb: R2.2, R3.1, TP9.1, U1.2 (-)
/Vref: R7.2, R8.2, R13.1, U1.5 (Ref), U2.2 (K)
GND: C4.2, J1.2, J2.2, J3.2, J5.2, J6.4, J6.10, J6.11, J7.5, Q3.2 (E), R3.2, R14.2, TP3.1, U1.4 (V-), U2.3 (A)
unnamed: D1.2 (A), D2.1 (K), K1.5, Q3.3 (C)
unnamed: D2.2 (A), R11.2
unnamed: J3.1, R6.2
unnamed: Q3.1 (B), R12.1
unnamed: R5.1, R7.1, U1.1 (RG)
unnamed: R13.2, R14.1, U2.1 (REF)

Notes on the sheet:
Select value of resistor in voltage divider Vb to be equal to the resistance of the sensor at the lowest temperature.
Relay switching circuit for controlling heating element.
Button Input
Heater Output
Test Points
Gain resistor is chosen such that the output voltage = max voltage at the maximum temperature expected (in this case 30°C).
Battery Input
Voltage Reference for Instrumentation Amplifier
ButtonInput
ADC input
LED indicator to show when the system is on.
5V would come from the microcontroller. Bat_In would come from the power supply. HeaterV lines would connect to the heating pads. https://www.instructables.com/Reading-Temperature-From-PT100-Using-Arduino/
PD2 used to switch through transistor. 5V supply for relay. COM and NO terminals connected to heeater.
GPIO output
Wheatstone bridge for sensor reading
HeaterControl
Pushbutton to start or stop operation of temperature controller.
TempReading
IndicatorControl
UART
Instrumentation amplifier as input to MCU
LED output

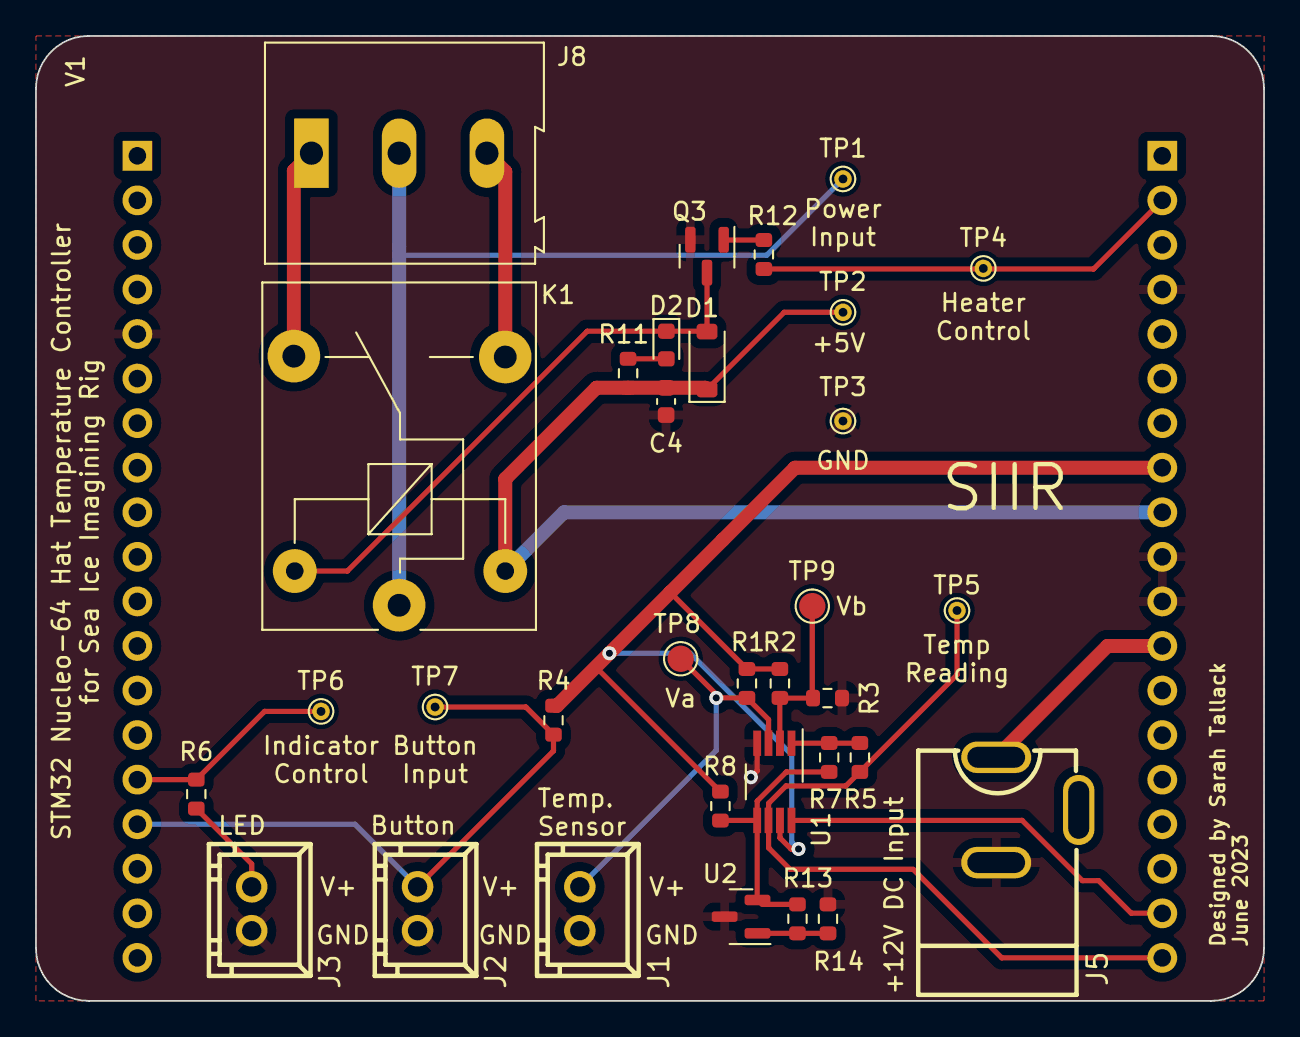
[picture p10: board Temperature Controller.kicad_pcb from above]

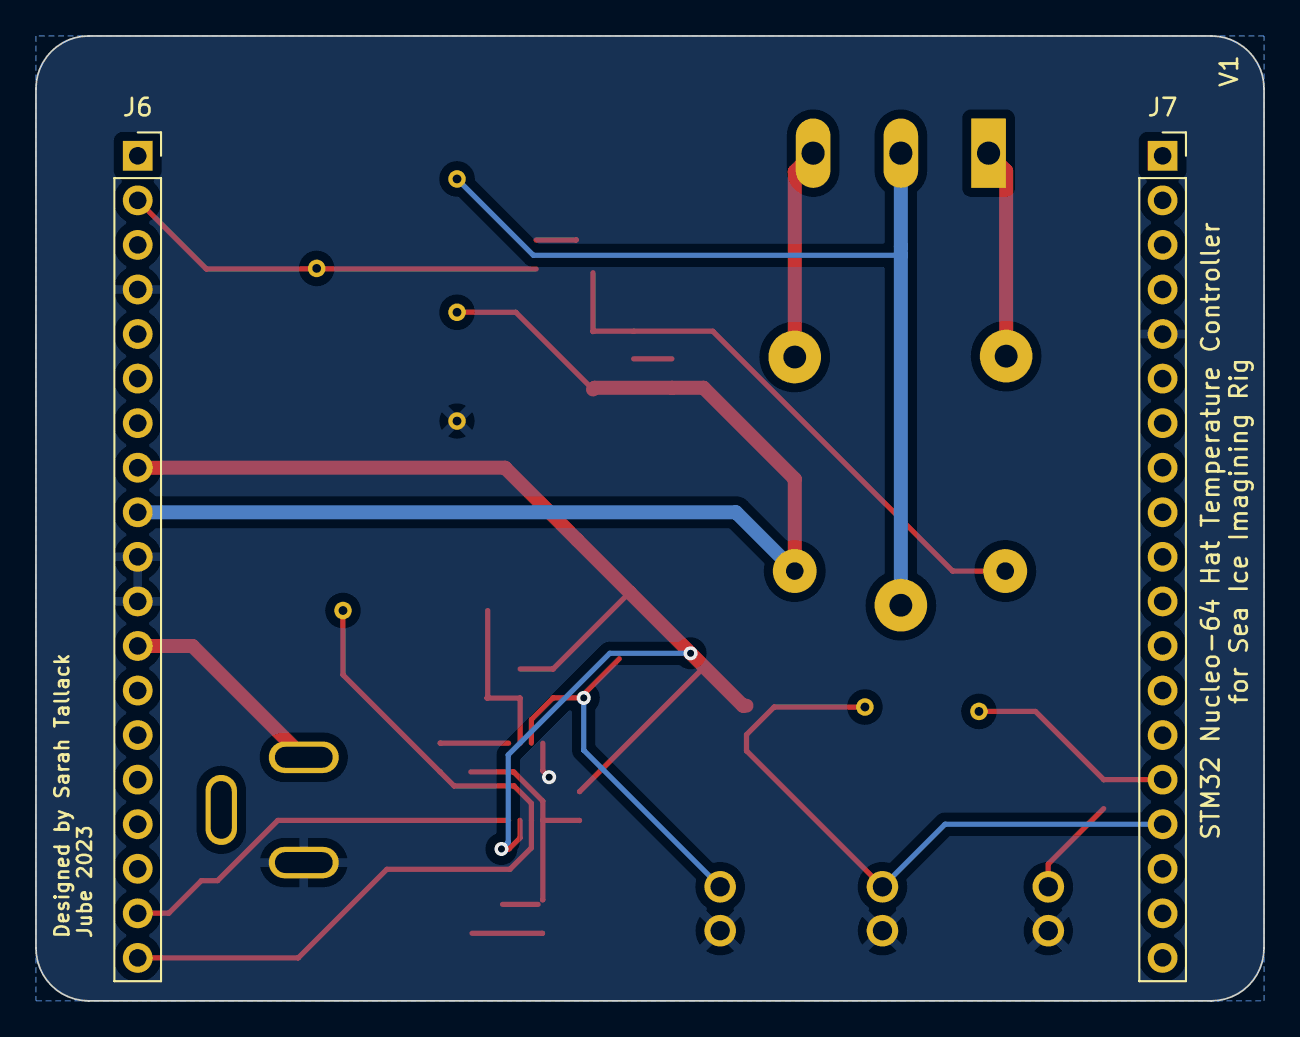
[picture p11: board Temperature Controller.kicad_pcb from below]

Board: 2 copper layers, 70.0 x 55.0 mm, 35 parts (2 on the bottom side), 21 nets.

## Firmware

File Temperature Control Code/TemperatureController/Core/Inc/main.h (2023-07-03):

/* USER CODE BEGIN Header */
/**
  ******************************************************************************
  * @file           : main.h
  * @brief          : Header for main.c file.
  *                   This file contains the common defines of the application.
  ******************************************************************************
  * @attention
  *
  * Copyright (c) 2022 STMicroelectronics.
  * All rights reserved.
  *
  * This software is licensed under terms that can be found in the LICENSE file
  * in the root directory of this software component.
  * If no LICENSE file comes with this software, it is provided AS-IS.
  *
  ******************************************************************************
  */
/* USER CODE END Header */

/* Define to prevent recursive inclusion -------------------------------------*/
#ifndef __MAIN_H
#define __MAIN_H

#ifdef __cplusplus
extern "C" {
#endif

/* Includes ------------------------------------------------------------------*/
#include "stm32l4xx_hal.h"

/* Private includes ----------------------------------------------------------*/
/* USER CODE BEGIN Includes */

/* USER CODE END Includes */

/* Exported types ------------------------------------------------------------*/
/* USER CODE BEGIN ET */

/* USER CODE END ET */

/* Exported constants --------------------------------------------------------*/
/* USER CODE BEGIN EC */

/* USER CODE END EC */

/* Exported macro ------------------------------------------------------------*/
/* USER CODE BEGIN EM */

/* USER CODE END EM */

/* Exported functions prototypes ---------------------------------------------*/
void Error_Handler(void);

/* USER CODE BEGIN EFP */

/* USER CODE END EFP */

/* Private defines -----------------------------------------------------------*/
#define B1_Pin GPIO_PIN_13
#define B1_GPIO_Port GPIOC
#define B1_EXTI_IRQn EXTI15_10_IRQn
#define TempReading_Pin GPIO_PIN_0
#define TempReading_GPIO_Port GPIOC
#define TempSensorControl_Pin GPIO_PIN_1
#define TempSensorControl_GPIO_Port GPIOC
#define LD2_Pin GPIO_PIN_5
#define LD2_GPIO_Port GPIOA
#define HeatControl_Pin GPIO_PIN_2
#define HeatControl_GPIO_Port GPIOD
#define ButtonInput_Pin GPIO_PIN_3
#define ButtonInput_GPIO_Port GPIOB
#define Indicator_Pin GPIO_PIN_5
#define Indicator_GPIO_Port GPIOB
/* USER CODE BEGIN Private defines */

/* USER CODE END Private defines */

#ifdef __cplusplus
}
#endif

#endif /* __MAIN_H */

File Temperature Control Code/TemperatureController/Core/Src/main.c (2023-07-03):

/* USER CODE BEGIN Header */
/**
  ******************************************************************************
  * Info: Temperature Controller for Sea Ice Project
  * Author: Sarah Tallack
  * Institution: University of Cape Town
  * Date: 9 December 2022
  ******************************************************************************
  * Program to implement a bang-bang controller for the regulation of temperature
  * for a battery enclosure. To check the reading of temperature, plug in the
  * Nucleo board via a micro-USB cable open a serial connection.
  *
  * The program reads an ADC value between 0 and 4095, which is then converted
  * into a voltage values, between 0V and 3.3V. This voltage value is an UART_Print
  * of a sensor circuit and has a direct relationship with the temperature being
  * sensed. More detail can be found in the Temperature Controller documentation.
  *
  * The temperature range is roughly - 23°C to 30°C. The following pins are used:
  * PB3: Button Input, which is programmed to an interrupt and power system on.
  * PB5: LED Indicator, to show when the system is powered on.
  * PC0: Temperature Reading, which is an ADC that gives a value related to temp.
  * PD2: Heater Control, GPIO UART_Print which is used to switch on power to external
  * 	 heaters.
  *	PA2 and PA3: UART communication for debugging.
  *	PA5: LD2, built in LED on board, default configuration.
  *	PC13: B1, button of board, default configuration.
  *
  *	To see the interrupt functions, see stm32l4xx_it.c file.
  ******************************************************************************
  */
/* USER CODE END Header */
/* Includes ------------------------------------------------------------------*/
#include "main.h"

/* Private includes ----------------------------------------------------------*/
/* USER CODE BEGIN Includes */
#include "inttypes.h"
#include "string.h"
#include "stdio.h"
/* USER CODE END Includes */

/* Private typedef -----------------------------------------------------------*/
/* USER CODE BEGIN PTD */

/* USER CODE END PTD */

/* Private define ------------------------------------------------------------*/
/* USER CODE BEGIN PD */
/* USER CODE END PD */

/* Private macro -------------------------------------------------------------*/
/* USER CODE BEGIN PM */

/* USER CODE END PM */

/* Private variables ---------------------------------------------------------*/
ADC_HandleTypeDef hadc1;

/* USER CODE BEGIN PV */

char print[25];			// array for printing via UART

uint32_t Volt;
int Temp;

uint8_t mode = 0;		// mode = 1 -> when button pressed
uint32_t Temp_low = 20;
uint32_t Temp_high = 25;
/* USER CODE END PV */

/* Private function prototypes -----------------------------------------------*/
void SystemClock_Config(void);
static void MX_GPIO_Init(void);
static void MX_ADC1_Init(void);
/* USER CODE BEGIN PFP */
uint32_t ADC_to_Volt(uint32_t ADC_val);
int Volt_to_Temp(uint32_t Volt);
void Control_Heater(int Temp);
void UART_Print(uint32_t val, uint8_t type);
/* USER CODE END PFP */

/* Private user code ---------------------------------------------------------*/
/* USER CODE BEGIN 0 */

/* USER CODE END 0 */

/**
  * @brief  The application entry point.
  * @retval int
  */
int main(void)
{
  /* USER CODE BEGIN 1 */

  /* USER CODE END 1 */

  /* MCU Configuration--------------------------------------------------------*/

  /* Reset of all peripherals, Initializes the Flash interface and the Systick. */
  HAL_Init();

  /* USER CODE BEGIN Init */

  /* USER CODE END Init */

  /* Configure the system clock */
  SystemClock_Config();

  /* USER CODE BEGIN SysInit */

  /* USER CODE END SysInit */

  /* Initialize all configured peripherals */
  MX_GPIO_Init();
  MX_ADC1_Init();
  /* USER CODE BEGIN 2 */

  /* USER CODE END 2 */

  /* Infinite loop */
  /* USER CODE BEGIN WHILE */
  while (1)
  {
    /* USER CODE END WHILE */

    /* USER CODE BEGIN 3 */

	while (mode == 1)
	{
		// Get ADC value
		HAL_ADC_Start(&hadc1);
		HAL_ADC_PollForConversion(&hadc1, HAL_MAX_DELAY);
		uint32_t ADC = HAL_ADC_GetValue(&hadc1);
		UART_Print(ADC, 0);

		// Convert ADC value to voltage
		Volt = ADC_to_Volt(ADC);
		UART_Print(Volt, 1);

		// Convert voltage value to temperature
		Temp = Volt_to_Temp(Volt);
		memset(print, 0, sizeof print);
		sprintf(print, "Temperature: %d\r\n", Temp);
		HAL_UART_Transmit(&huart2, print, sizeof(print), 1000);

		// Use temperature to control UART_Print
		Control_Heater(Temp);
		HAL_Delay(100);
	}
	/*
	// Get ADC value
	HAL_ADC_Start(&hadc1);
	HAL_ADC_PollForConversion(&hadc1, HAL_MAX_DELAY);
	uint32_t ADC = HAL_ADC_GetValue(&hadc1);
	UART_Print(ADC, 0);

	// Convert ADC value to voltage
	Volt = ADC_to_Volt(ADC);
	UART_Print(Volt, 1);

	// Convert voltage value to temperature
	Temp = Volt_to_Temp(Volt);
	memset(print, 0, sizeof print);
	sprintf(print, "Temperature: %d\r\n", Temp);
	HAL_UART_Transmit(&huart2, print, sizeof(print), 1000);

	// Use temperature to control UART_Print
	Control_Heater(Temp);
	HAL_Delay(tDelay);

	if (Temp >= 20){
		HAL_GPIO_TogglePin(GPIOA, GPIO_PIN_5); // Toggle blue LED PA5
		//HAL_Delay(tDelay);
	}*/


  }
  /* USER CODE END 3 */
}

/**
  * @brief System Clock Configuration
  * @retval None
  */
void SystemClock_Config(void)
{
  RCC_OscInitTypeDef RCC_OscInitStruct = {0};
  RCC_ClkInitTypeDef RCC_ClkInitStruct = {0};

  /** Configure the main internal regulator output voltage
  */
  if (HAL_PWREx_ControlVoltageScaling(PWR_REGULATOR_VOLTAGE_SCALE1) != HAL_OK)
  {
    Error_Handler();
  }

  /** Initializes the RCC Oscillators according to the specified parameters
  * in the RCC_OscInitTypeDef structure.
  */
  RCC_OscInitStruct.OscillatorType = RCC_OSCILLATORTYPE_MSI;
  RCC_OscInitStruct.MSIState = RCC_MSI_ON;
  RCC_OscInitStruct.MSICalibrationValue = 0;
  RCC_OscInitStruct.MSIClockRange = RCC_MSIRANGE_6;
  RCC_OscInitStruct.PLL.PLLState = RCC_PLL_NONE;
  if (HAL_RCC_OscConfig(&RCC_OscInitStruct) != HAL_OK)
  {
    Error_Handler();
  }

  /** Initializes the CPU, AHB and APB buses clocks
  */
  RCC_ClkInitStruct.ClockType = RCC_CLOCKTYPE_HCLK|RCC_CLOCKTYPE_SYSCLK
                              |RCC_CLOCKTYPE_PCLK1|RCC_CLOCKTYPE_PCLK2;
  RCC_ClkInitStruct.SYSCLKSource = RCC_SYSCLKSOURCE_MSI;
  RCC_ClkInitStruct.AHBCLKDivider = RCC_SYSCLK_DIV1;
  RCC_ClkInitStruct.APB1CLKDivider = RCC_HCLK_DIV1;
  RCC_ClkInitStruct.APB2CLKDivider = RCC_HCLK_DIV1;

  if (HAL_RCC_ClockConfig(&RCC_ClkInitStruct, FLASH_LATENCY_0) != HAL_OK)
  {
    Error_Handler();
  }
}

/**
  * @brief ADC1 Initialization Function
  * @param None
  * @retval None
  */
static void MX_ADC1_Init(void)
{

  /* USER CODE BEGIN ADC1_Init 0 */

  /* USER CODE END ADC1_Init 0 */

  ADC_MultiModeTypeDef multimode = {0};
  ADC_ChannelConfTypeDef sConfig = {0};

  /* USER CODE BEGIN ADC1_Init 1 */

  /* USER CODE END ADC1_Init 1 */

  /** Common config
  */
  hadc1.Instance = ADC1;
  hadc1.Init.ClockPrescaler = ADC_CLOCK_ASYNC_DIV1;
  hadc1.Init.Resolution = ADC_RESOLUTION_12B;
  hadc1.Init.DataAlign = ADC_DATAALIGN_RIGHT;
  hadc1.Init.ScanConvMode = ADC_SCAN_DISABLE;
  hadc1.Init.EOCSelection = ADC_EOC_SINGLE_CONV;
  hadc1.Init.LowPowerAutoWait = DISABLE;
  hadc1.Init.ContinuousConvMode = DISABLE;
  hadc1.Init.NbrOfConversion = 1;
  hadc1.Init.DiscontinuousConvMode = DISABLE;
  hadc1.Init.ExternalTrigConv = ADC_SOFTWARE_START;
  hadc1.Init.ExternalTrigConvEdge = ADC_EXTERNALTRIGCONVEDGE_NONE;
  hadc1.Init.DMAContinuousRequests = DISABLE;
  hadc1.Init.Overrun = ADC_OVR_DATA_PRESERVED;
  hadc1.Init.OversamplingMode = DISABLE;
  if (HAL_ADC_Init(&hadc1) != HAL_OK)
  {
    Error_Handler();
  }

  /** Configure the ADC multi-mode
  */
  multimode.Mode = ADC_MODE_INDEPENDENT;
  if (HAL_ADCEx_MultiModeConfigChannel(&hadc1, &multimode) != HAL_OK)
  {
    Error_Handler();
  }

  /** Configure Regular Channel
  */
  sConfig.Channel = ADC_CHANNEL_1;
  sConfig.Rank = ADC_REGULAR_RANK_1;
  sConfig.SamplingTime = ADC_SAMPLETIME_2CYCLES_5;
  sConfig.SingleDiff = ADC_SINGLE_ENDED;
  sConfig.OffsetNumber = ADC_OFFSET_NONE;
  sConfig.Offset = 0;
  if (HAL_ADC_ConfigChannel(&hadc1, &sConfig) != HAL_OK)
  {
    Error_Handler();
  }
  /* USER CODE BEGIN ADC1_Init 2 */

  /* USER CODE END ADC1_Init 2 */

}

/**
  * @brief GPIO Initialization Function
  * @param None
  * @retval None
  */
static void MX_GPIO_Init(void)
{
  GPIO_InitTypeDef GPIO_InitStruct = {0};

  /* GPIO Ports Clock Enable */
  __HAL_RCC_GPIOC_CLK_ENABLE();
  __HAL_RCC_GPIOH_CLK_ENABLE();
  __HAL_RCC_GPIOA_CLK_ENABLE();
  __HAL_RCC_GPIOD_CLK_ENABLE();
  __HAL_RCC_GPIOB_CLK_ENABLE();

  /*Configure GPIO pin Output Level */
  HAL_GPIO_WritePin(TempSensorControl_GPIO_Port, TempSensorControl_Pin, GPIO_PIN_RESET);

  /*Configure GPIO pin Output Level */
  HAL_GPIO_WritePin(LD2_GPIO_Port, LD2_Pin, GPIO_PIN_RESET);

  /*Configure GPIO pin Output Level */
  HAL_GPIO_WritePin(HeatControl_GPIO_Port, HeatControl_Pin, GPIO_PIN_RESET);

  /*Configure GPIO pin Output Level */
  HAL_GPIO_WritePin(Indicator_GPIO_Port, Indicator_Pin, GPIO_PIN_RESET);

  /*Configure GPIO pin : B1_Pin */
  GPIO_InitStruct.Pin = B1_Pin;
  GPIO_InitStruct.Mode = GPIO_MODE_IT_RISING;
  GPIO_InitStruct.Pull = GPIO_NOPULL;
  HAL_GPIO_Init(B1_GPIO_Port, &GPIO_InitStruct);

  /*Configure GPIO pin : PC14 */
  GPIO_InitStruct.Pin = GPIO_PIN_14;
  GPIO_InitStruct.Mode = GPIO_MODE_INPUT;
  GPIO_InitStruct.Pull = GPIO_NOPULL;
  HAL_GPIO_Init(GPIOC, &GPIO_InitStruct);

  /*Configure GPIO pin : TempSensorControl_Pin */
  GPIO_InitStruct.Pin = TempSensorControl_Pin;
  GPIO_InitStruct.Mode = GPIO_MODE_OUTPUT_PP;
  GPIO_InitStruct.Pull = GPIO_NOPULL;
  GPIO_InitStruct.Speed = GPIO_SPEED_FREQ_LOW;
  HAL_GPIO_Init(TempSensorControl_GPIO_Port, &GPIO_InitStruct);

  /*Configure GPIO pin : LD2_Pin */
  GPIO_InitStruct.Pin = LD2_Pin;
  GPIO_InitStruct.Mode = GPIO_MODE_OUTPUT_PP;
  GPIO_InitStruct.Pull = GPIO_NOPULL;
  GPIO_InitStruct.Speed = GPIO_SPEED_FREQ_LOW;
  HAL_GPIO_Init(LD2_GPIO_Port, &GPIO_InitStruct);

  /*Configure GPIO pin : HeatControl_Pin */
  GPIO_InitStruct.Pin = HeatControl_Pin;
  GPIO_InitStruct.Mode = GPIO_MODE_OUTPUT_PP;
  GPIO_InitStruct.Pull = GPIO_NOPULL;
  GPIO_InitStruct.Speed = GPIO_SPEED_FREQ_LOW;
  HAL_GPIO_Init(HeatControl_GPIO_Port, &GPIO_InitStruct);

  /*Configure GPIO pin : ButtonInput_Pin */
  GPIO_InitStruct.Pin = ButtonInput_Pin;
  GPIO_InitStruct.Mode = GPIO_MODE_IT_RISING;
  GPIO_InitStruct.Pull = GPIO_NOPULL;
  HAL_GPIO_Init(ButtonInput_GPIO_Port, &GPIO_InitStruct);

  /*Configure GPIO pin : Indicator_Pin */
  GPIO_InitStruct.Pin = Indicator_Pin;
  GPIO_InitStruct.Mode = GPIO_MODE_OUTPUT_PP;
  GPIO_InitStruct.Pull = GPIO_NOPULL;
  GPIO_InitStruct.Speed = GPIO_SPEED_FREQ_LOW;
  HAL_GPIO_Init(Indicator_GPIO_Port, &GPIO_InitStruct);

  /* EXTI interrupt init*/
  HAL_NVIC_SetPriority(EXTI15_10_IRQn, 0, 0);
  HAL_NVIC_EnableIRQ(EXTI15_10_IRQn);

}

/* USER CODE BEGIN 4 */
uint32_t ADC_to_Volt(uint32_t ADC_val){
	uint32_t volt = ADC_val*3300/4095;
	return volt;
}

int Volt_to_Temp(uint32_t Volt){
	/* Get temperature from ADC voltage
	 *
	 * Vin = 3.3 V
	 * R0 = 100 ohm
	 * G = 1 + 2 * 24.7k/R3, R3 = 91 ohms, 24.7k from instrumentation amplifier datasheet
	 * Vb = Vin*R3/(R3+3.3k)
	 * Determine output of sensor voltage divider
	 * Va = Volt/G + Vb
	 *
	 * Find resistance of temperature sensor
	 * Rt = 3.3k*Va/(Vin - Va)
	 *
	 * Calculate temperature from resistor/temperature relationship
	 * temp = (Rt/R0 - 1)/0.00385
	 *
	*/

	// Combine the above formulae into on as C doesn't like the seperate equations :(
	int temp = (3300/100 * (Volt/165.66667 + 88.5579)/(3300-(Volt/165.66667 + 88.5579)) - 1)/0.00385;
	return temp;
}

void Control_Heater(int Temp){
	if (Temp > Temp_high){
		// When reading goes above 25°C turn off
		HAL_GPIO_WritePin(GPIOD, GPIO_PIN_2, GPIO_PIN_RESET);
	}
	else if (Temp < Temp_low){
		// When reading goes below 20°C turn on
		HAL_GPIO_WritePin(GPIOD, GPIO_PIN_2, GPIO_PIN_SET);
	}
}
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

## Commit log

2023-03-29 Temp controller and power distribution PCBS and temp controller code
    [2 Pin Header.obj, 2 Pin Male Header.kicad_pcb, 3 Pin Male Header.kicad_pcb, BOM-Power Distribution.csv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]
2023-03-29 Added power budget
    [PowerBudget.xlsx]
2023-03-29 populated power budget
    [PowerBudget.xlsx]
